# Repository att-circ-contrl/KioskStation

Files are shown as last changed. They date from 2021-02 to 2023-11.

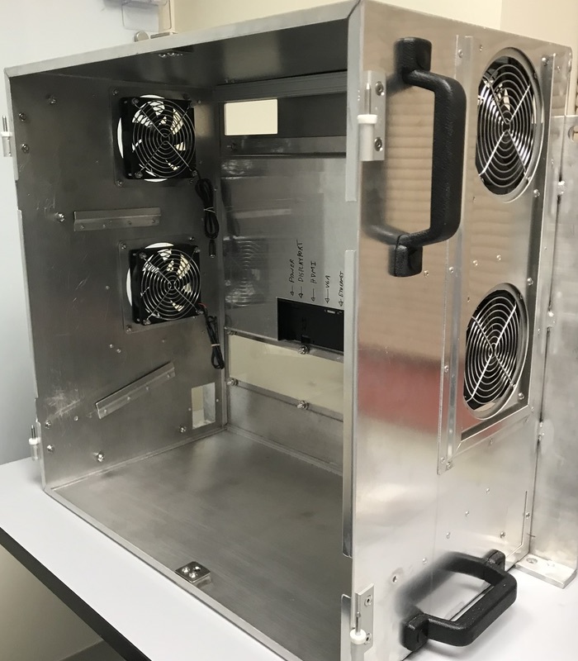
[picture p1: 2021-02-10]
photos/install-20181106/fan-installed.jpg

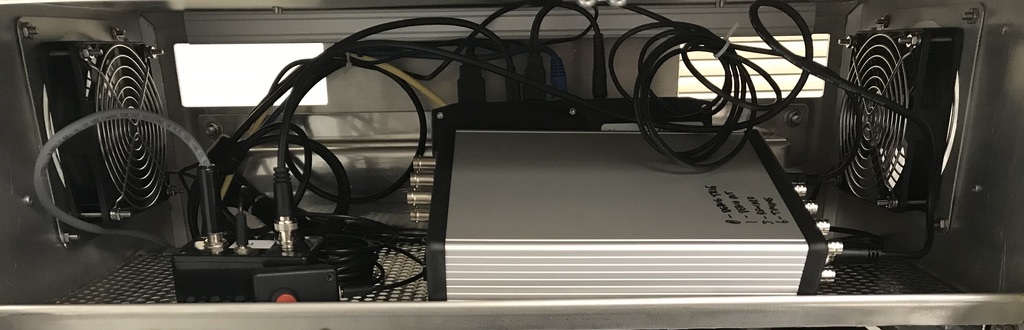
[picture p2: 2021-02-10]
photos/install-20181106/ard-pbox-wiring.jpg

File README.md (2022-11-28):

# "Kiosk Station" NHP Game Kiosk

## Overview

The "Kiosk Station" is an interactive game kiosk intended for use with
non-human primates. The kiosk is mounted to one module of an apartment-cage
(replacing one of the wall panels), allowing a monkey to freely play the
game without direct supervision.

**This repository is a work-in-progress.**
All of the CAD files and auxiliary information needed to make additional
"revision 2" kiosks should be present (in `drawings-ext/rev2-cad-2021`),
but organization could be better.

The "Kiosk Station" project is copyright (c) 2021 by Vanderbilt University,
and is released under the Creative Commons Attribution 4.0 International
License.

## Folders

This repository contains the following directories:

* `datasheets` -- Vendor-supplied datasheets. Under vendor copyright.
* `drawings-ext` --
CAD files and screenshots for various versions of the Kiosk Station.
Component models and documentation provided by third-party component vendors
are under vendor copyright.
* `drawings` -- Assorted mechanical drawings.
* `manual` --
LaTeX source and PDF output for the kiosk user manual (incomplete).
* `notes` -- Assorted notes regarding the kiosk's design and components.
* `photos` -- Representative photos of the kiosk and kiosk equipment.
* `proximity-2017` --
Materials relating to tests of proximity sensors that were to be mounted
on the sipper tube of the kiosk.
* `pump-box` --
Design documents for the control box for the LMI fluid pump used with the
kiosk. The intention is that TTL pulses or user-fob button presses can
trigger delivery of a fluid reward (water or juice) through the sipper tube.
* `reference` --
Assorted reference documents (other than datasheets or vendor-supplied
materials).
* `vendor-docs` --
Vendor-provided documentation (other than datasheets). Under vendor copyright.
* `wiring-diagrams` -- Wiring/cabling diagrams for kiosk-related equipment.

_This is the end of the file._

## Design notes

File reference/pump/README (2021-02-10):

Executive summary:

- Pinout is on page 17 of the manual, control scheme is on page 21.
- Connector type is "M12" circular connector.

- Use their grey cable if possible (p/n 48414).
- White wire is ground, brown is _enable (short to ground), blue is pulse 
(short to ground; pump triggers on release). Black is +15v (use for power),
green is analog control (nc for this pump type).

- Max voltage 24 V, max current 15 mA. They used a 10 kOhm PD in their 
"adapter cable", so actual currents are likely much lower.
- Pulse times must be at least 50 ms.

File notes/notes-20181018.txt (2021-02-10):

From 18 Oct 2018 paper notes:

- Holes in viewport plates should be larger for more alignment slop; some of 
the plates are very difficult to remove due to rubbing on threads.

- Pump mounting brackets should be 1" rather than 1.5" wide, to avoid 
conflict with anything else attached to the 1" extrusion.

- Fan mounts need an adapter plate for 120mm fans (implemented as 6" fans).

- Cannot mount twist-style t-slot cable holders to 1" rail due to enclosure 
sheet metal extending past the edge of the extrusion; trim if possible.

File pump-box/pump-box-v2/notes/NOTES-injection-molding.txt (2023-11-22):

I'm designing the v2 case as something that could be manufactured by
injection molding, in case we want lots of these.

The main difficulty is that it'll have to be 3 pieces rather than 2 pieces,
if we want the cable gland to enter through the end. Entering through a face
could be 2 pieces.

For injection molding, thickness should be uniform (if possible), with a
draft angle of about 4 degrees on vertical surfaces where practical.

For parts to be released from the mold (and for the molds to be machined),
each half of the mold has to be "2.5-d" (no undercuts). This means each half
of the part being made needs to be "2.5-d". "Flying saucer" (with the part
lin on the rim) and "bowl" (with the part line on the lip) shapes are
examples of this type of geometry.

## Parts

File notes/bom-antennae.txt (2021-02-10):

Suitable parts for hooking up a router to an external antenna:

Item			Digikey p/n		Each	Qty	Total

cable 4' RP-SMA RA	JR2R3-L1-4F-ND		34.00	1	34.00
antenna dome RP-SMA	ANT-DB1-WRT-MON-RPS-ND	12.94	1	12.94
Washer 1/2" galv	H840-ND			0.0309	2	0.06

Total:								47.00

Suitable parts for hooking up a Unity computer to an external antenna:

Item			Digikey p/n		Each	Qty	Total

cable 20" IPEX MHF4/SMA	1837-1033-ND		3.25	1	3.25
antenna dome SMA	ANT-DB1-WRT-MON-SMA-ND	12.94	1	12.94
Washer 1/2" galv	H840-ND			0.0309	2	0.06

Total:								16.25

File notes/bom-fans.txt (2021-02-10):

Fan parts from 20181004-digikey:

fan 120mm 12V 34dBA:	259-1472-nd
medical 12V 2A wart:	1145-1240-nd
barrel splitter 2.1mm:	1528-1455-nd
barrel 2.1mm F to wire:	839-1145-nd

From 2021:

fan 80mm 12V 33dBA:	259-1629-nd

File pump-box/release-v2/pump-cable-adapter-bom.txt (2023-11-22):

Bill of materials for the v2 pump control dongle:

Item				Mfg p/n		Digikey p/n		Qty

transistor NPN SOT-23-3		SST3904T116	SST3904T116CT-ND	2

resistor 0805 10 kOhm		RC0805FR-0710KL	311-10.0KCRCT-ND	2

jack audio 3.5mm mono SMT	MJ-3523-SMT-TR	CP-3523MJCT-ND		1

BNC jack (PCB R/A)		0731000154	WM5281-ND		1

terminal block 3.81mm 5pos	284392-5	A98169-ND		1

cable cland PG9			3210		3720-3210-ND		1
(NOTE - 3211 is a fallback option. 3210 is black, 3211 is grey.)

(This is the end of the file.)

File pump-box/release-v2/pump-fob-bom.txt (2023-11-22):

Bill of materials for the v2 pump trigger fob:

Item				Mfg p/n		Digikey p/n		Qty

jack audio 3.5mm mono SMT	MJ-3523-SMT-TR	CP-3523MJCT-ND		1

switch smt 12mm spst		K12SCS1.55NOLFTX	CKN10790CT-ND	1

(This is the end of the file.)

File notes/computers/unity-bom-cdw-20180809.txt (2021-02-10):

Machine (no RAM):  NUC6i7KYK  CDW p/n: 4085713   (543.99 USD)
RAM:  Kingston DDR4 2x4gig  CDW p/n: 4039935   (102.99 USD)
SSD:  (1 TB) Samsung MZ-N6E1T0BW  CDW p/n: 4934196   (239.99 USD)
Network cable:  Tripp Lite 3' Cat5e  CDW p/n: 324473  (2.99 USD)

Unit cost:  889.96 USD

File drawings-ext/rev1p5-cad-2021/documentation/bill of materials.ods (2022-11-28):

name | number | qty per | total
Positioning arm | 47065t361 | 4 | 8
black rubber handle | 13665a27 | 4 | 8
left hinge | 3116a1 | 2 | 4
right hinge | 3116a2 | 2 | 4
slam latch | 171hn01 | 5 | 10
low profile clamp | 84865a22 | 16 | 32
90 bracket | 5537t349 | 2 | 4
surface mount hinge | 1624a52 | 2 | 4
t handle latch | 11055a24 | 1 | 2
t slot extrusion (2 sided) | 47065t551 | 5 | 10
stainless studs ¼-20
stainless studs 10-32 3/8 | CD51032-0375-1 (https://michigan.hybrocosales.com/details/item?itemid=CD51032-0375-1)
Stainless studs 3/8-16 1” | CD53816-1000-1
aluminum studs ¼ -20 3/4” | CD51420-0750-1 (https://michigan.hybrocosales.com/details/item?itemid=CD51420-0750-1)
stainless nuts ¼ -20
stainless nuts 10-32
stainless nuts 3/8 -16
stainless washers ¼
stainless washers 3/8
stainless washers #10
stainless angle 1 ¼ x 1 ¼
stainless angle 1x1
stainless rod ½
stainless rod 3/8
stainless rod ¼
stainless flatbar 1 x 3/16
stainless flatbar 1.5 x 1/8
stainless flatbar 1.5 x 5/16
stainless tubing 1”
stainless sch 40 pipe 3.5”
stainless sq tube ½
stainless rnd tube 1/8”
aluminum flattened expanded
stainless button head bolt ¼ -20 ¾
stainless button head bolt ¼ -20 ½
stainless bolt 3/8-16
Stainless 10-32 button ½
stainless screw #8 5/16
stainless countersink ¼ 20 3/8
stainless countersink10-32 3/8
plexiglas
panels

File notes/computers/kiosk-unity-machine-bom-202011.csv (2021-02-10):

Please save as excel file & upload to Procurement Notification form. |  |  |  | ORDER TOTAL |  | $2,299.88
Enter the ORDER TOTAL amount listed here into the field 'Quote/Line Item Worksheet Total' in the online Procurement Notification form.
Line | Item Catalog Number | Item Description including specs & customizations | Quantity | Unit Price | UoM | Extended Price | Item URL
 |  |  |  |  | Each
 |  |  |  |  | Case/Carton
1 | 5033016 | computer NUC8i7HVK barebones small form factor | 2 | $908.99 | Each | $1,817.98 | https://www.cdw.com/product/intel-next-unit-of-computing-kit-nuc8i7hvk-mini-pc-core-i7-8809g-3.1-gh/5033016
2 | 4934196 | SSD 1 TB 860 EVO | 2 | $149.99 | Each | $299.98 | https://www.cdw.com/product/samsung-860-evo-mz-n6e1t0bw-solid-state-drive-1-tb-sata-6gb-s/4934196
3 | 5109903 | SDRAM DDR4 SODIMM-260 16 GB non-ECC | 2 | $69.99 | Each | $139.98 | https://www.cdw.com/product/kingston-ddr4-16-gb-so-dimm-260-pin-unbuffered/5109903
4 | 324473 | network cable cat5e 3ft | 2 | $2.99 | Each | $5.98 | https://www.cdw.com/product/tripp-lite-3ft-cat5e-cat5-350mhz-blue-snagless-molded-patch-cable-rj45-m-m/324473
5 | 4639758 | cable mini-DP to DP 3ft | 2 | $8.99 | Each | $17.98 | https://www.cdw.com/product/tripp-lite-mini-displayport-to-displayport-adapter-cable-4k-m-m-black-3ft/4639758
6 | 4884365 | cable HDMI 3ft | 2 | $8.99 | Each | $17.98 | https://www.cdw.com/product/tripp-lite-high-speed-hdmi-cable-w-gripping-connectors-4k-m-m-black-3ft/4884365
7 |  |  |  |  |  | $-
8 |  |  |  |  |  | $-
9 |  |  |  |  |  | $-
10 |  |  |  |  |  | $-
11 |  |  |  |  |  | $-
12 |  |  |  |  |  | $-
13 |  |  |  |  |  | $-
14 |  |  |  |  |  | $-
15 |  |  |  |  |  | $-
16 |  |  |  |  |  | $-
17 |  |  |  |  |  | $-
18 |  |  |  |  |  | $-
19 |  |  |  |  |  | $-
20 |  |  |  |  |  | $-
21 |  |  |  |  |  | $-
22 |  |  |  |  |  | $-
23 |  |  |  |  |  | $-
24 |  |  |  |  |  | $-
25 |  |  |  |  |  | $-
26 |  |  |  |  |  | $-
27 |  |  |  |  |  | $-
28 |  |  |  |  |  | $-
29 |  |  |  |  |  | $-
30 |  |  |  |  |  | $-
31 |  |  |  |  |  | $-
32 |  |  |  |  |  | $-
33 |  |  |  |  |  | $-
34 |  |  |  |  |  | $-
35 |  |  |  |  |  | $-
36 |  |  |  |  |  | $-
37 |  |  |  |  |  | $-
38 |  |  |  |  |  | $-
39 |  |  |  |  |  | $-
40 |  |  |  |  |  | $-
41 |  |  |  |  |  | $-
42 |  |  |  |  |  | $-
43 |  |  |  |  |  | $-
44 |  |  |  |  |  | $-
45 |  |  |  |  |  | $-
46 |  |  |  |  |  | $-
47 |  |  |  |  |  | $-
48 |  |  |  |  |  | $-
49 |  |  |  |  |  | $-
50 |  |  |  |  |  | $-
51 |  |  |  |  |  | $-
52 |  |  |  |  |  | $-
53 |  |  |  |  |  | $-
54 |  |  |  |  |  | $-
55 |  |  |  |  |  | $-
56 |  |  |  |  |  | $-
57 |  |  |  |  |  | $-
58 |  |  |  |  |  | $-
59 |  |  |  |  |  | $-
60 |  |  |  |  |  | $-
61 |  |  |  |  |  | $-
62 |  |  |  |  |  | $-
63 |  |  |  |  |  | $-
64 |  |  |  |  |  | $-
65 |  |  |  |  |  | $-
66 |  |  |  |  |  | $-
67 |  |  |  |  |  | $-
68 |  |  |  |  |  | $-
69 |  |  |  |  |  | $-
70 |  |  |  |  |  | $-
71 |  |  |  |  |  | $-
72 |  |  |  |  |  | $-
73 |  |  |  |  |  | $-
74 |  |  |  |  |  | $-
75 |  |  |  |  |  | $-
76 |  |  |  |  |  | $-
77 |  |  |  |  |  | $-
78 |  |  |  |  |  | $-
79 |  |  |  |  |  | $-
80 |  |  |  |  |  | $-
81 |  |  |  |  |  | $-
82 |  |  |  |  |  | $-
83 |  |  |  |  |  | $-
84 |  |  |  |  |  | $-
85 |  |  |  |  |  | $-
86 |  |  |  |  |  | $-
87 |  |  |  |  |  | $-
88 |  |  |  |  |  | $-
89 |  |  |  |  |  | $-
90 |  |  |  |  |  | $-
91 |  |  |  |  |  | $-
92 |  |  |  |  |  | $-
93 |  |  |  |  |  | $-
94 |  |  |  |  |  | $-
95 |  |  |  |  |  | $-
96 |  |  |  |  |  | $-
97 |  |  |  |  |  | $-
98 |  |  |  |  |  | $-
99 |  |  |  |  |  | $-
100 |  |  |  |  |  | $-
 |  |  |  |  |  | $-
 |  |  |  |  |  | $-
 |  |  |  |  |  | $-
 |  |  |  |  |  | $-
 |  |  |  |  |  | $-
 |  |  |  |  |  | $-
 |  |  |  |  |  | $-
 |  |  |  |  |  | $-
 |  |  |  |  |  | $-
 |  |  |  |  |  | $-
 |  |  |  |  |  | $-
 |  |  |  |  |  | $-
 |  |  |  |  |  | $-
 |  |  |  |  |  | $-
 |  |  |  |  |  | $-
 |  |  |  |  |  | $-
 |  |  |  |  |  | $-
 |  |  |  |  |  | $-
 |  |  |  |  |  | $-
 |  |  |  |  |  | $-
 |  |  |  |  |  | $-
 |  |  |  |  |  | $-
 |  |  |  |  |  | $-
 |  |  |  |  |  | $-
 |  |  |  |  |  | $-
 |  |  |  |  |  | $-
 |  |  |  |  |  | $-
 |  |  |  |  |  | $-
 |  |  |  |  |  | $-
 |  |  |  |  |  | $-
 |  |  |  |  |  | $-
 |  |  |  |  |  | $-
 |  |  |  |  |  | $-
 |  |  |  |  |  | $-
 |  |  |  |  |  | $-
 |  |  |  |  |  | $-
 |  |  |  |  |  | $-
 |  |  |  |  |  | $-
 |  |  |  |  |  | $-
 |  |  |  |  |  | $-
 |  |  |  |  |  | $-
 |  |  |  |  |  | $-
 |  |  |  |  |  | $-
 |  |  |  |  |  | $-
 |  |  |  |  |  | $-
 |  |  |  |  |  | $-
 |  |  |  |  |  | $-
 |  |  |  |  |  | $-
 |  |  |  |  |  | $-
 |  |  |  |  |  | $-
 |  |  |  |  |  | $-
 |  |  |  |  |  | $-

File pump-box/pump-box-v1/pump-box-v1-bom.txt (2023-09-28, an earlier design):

Bill of materials for the v1 pump control box:

Item                         Digikey p/n     Unit Price     Qty      Cost

box 3.25x2.25x1.5"           HM113-ND           5.56         1       5.56
box 2x1.5.0.75"              HM375-ND           2.62         1       2.62

transistor NPN TO-92         2N3904FS-ND        0.21         2       0.42

resistor 1/4 W 10 kohm       10.0KXBK-ND        0.10         2       0.20
resistor 1/4 W 3.3 kohm      3.3KXBK-ND         0.10         1       0.10

proto board 1x1"             1568-1652-ND       1.50         1       1.50

screw 4-40 nylon 1/4"        H542-ND            0.09         1       0.09
standoff nylon 4-40 F/F 1/2" 36-1902C-ND        0.70         1       0.70
screw metal 4-40 3/8"        HM1456-ND          0.11         1       0.11

jack BNC panel mount         ARFX1064-ND        2.64         1       2.64
jack audio 1/4" stereo panel SC1563-ND          3.06         1       3.06
plug audio 1/4" stereo       SC1081-ND          4.39         1       4.39
jack audio 3.5mm mono panel  SC238-ND           2.54         2       5.08

cable audio 3.5mm M/M 10'    TL634-ND           4.61         1       4.61

button spst-no panel mount   CW158-ND           4.25         1       4.25

Total:                                                              35.33

NOTE - Digikey M12 cables have the wrong polarization key for the pump. We
need "reverse key" cables.
MEC-5FP-2M from www.mencom.com looks correct.

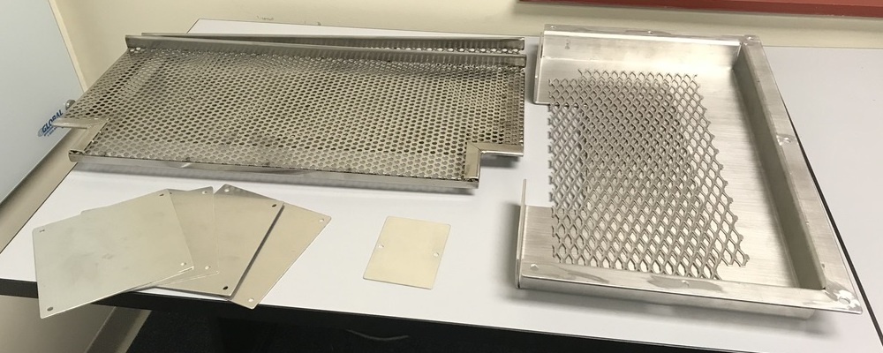
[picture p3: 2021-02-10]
photos/install-20181106/bay-parts.jpg

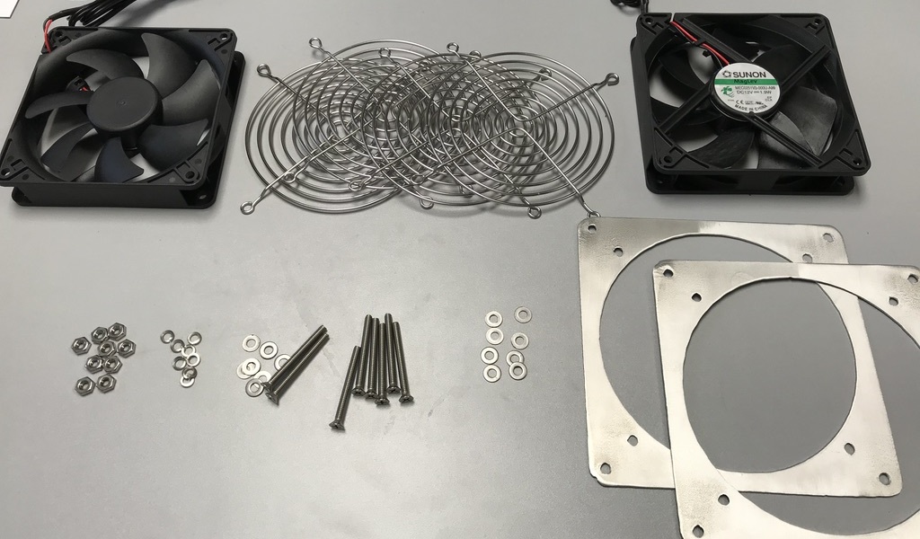
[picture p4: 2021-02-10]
photos/install-20181106/fan-parts.jpg

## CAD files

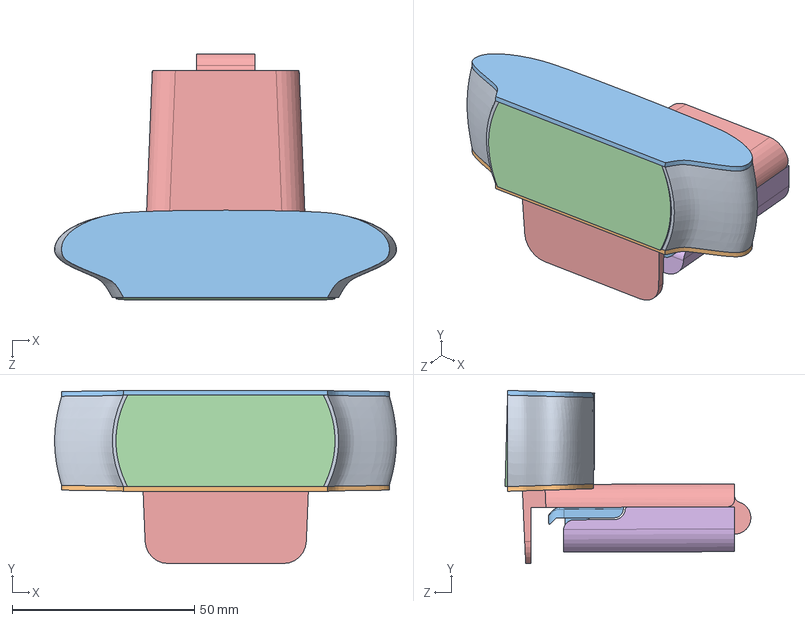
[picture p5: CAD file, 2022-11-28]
drawings-ext/rev1p5-cad-2021/camera/c920.SLDASM
93.8 x 47.5 x 67.5 mm
BOTTOM plate
TOP plate
Pieza4^c920
Top Holder
Pieza6^c920
Speaker^PCB_and_lens x 2
Lens Mount^PCB_and_lens
Pieza4^PCB_and_lens
Pieza8^c920

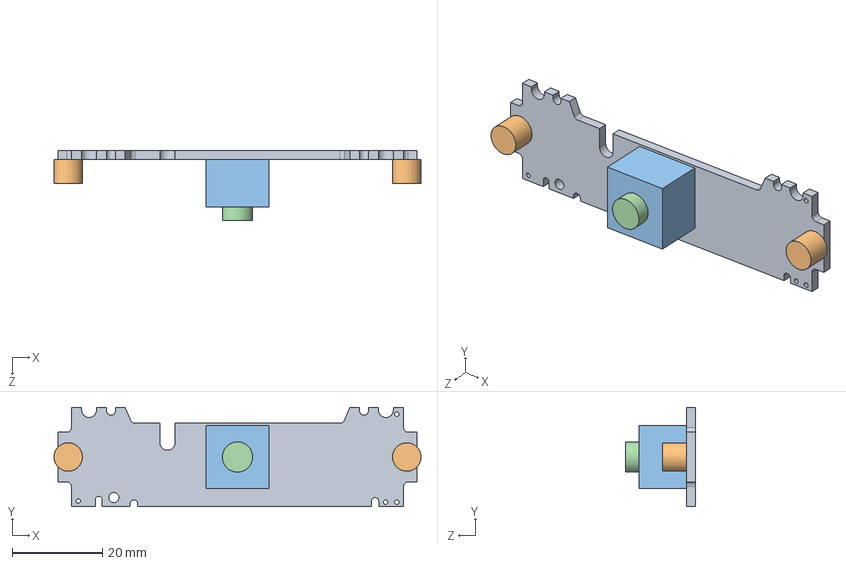
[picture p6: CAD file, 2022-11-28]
drawings-ext/rev1p5-cad-2021/camera/PCB_and_lens.SLDASM
81.3 x 22.0 x 15.5 mm
PCB^PCB_and_lens
Speaker^PCB_and_lens x 2
Lens Mount^PCB_and_lens
Pieza4^PCB_and_lens

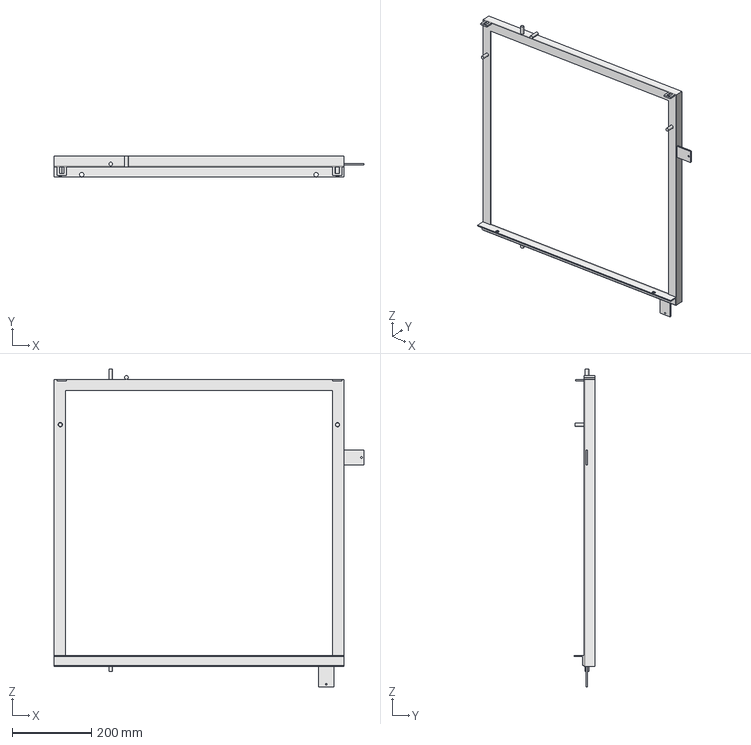
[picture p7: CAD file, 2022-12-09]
cad/adapter-rev2/adapter-rev2.fcstd
781.1 x 54.0 x 800.1 mm

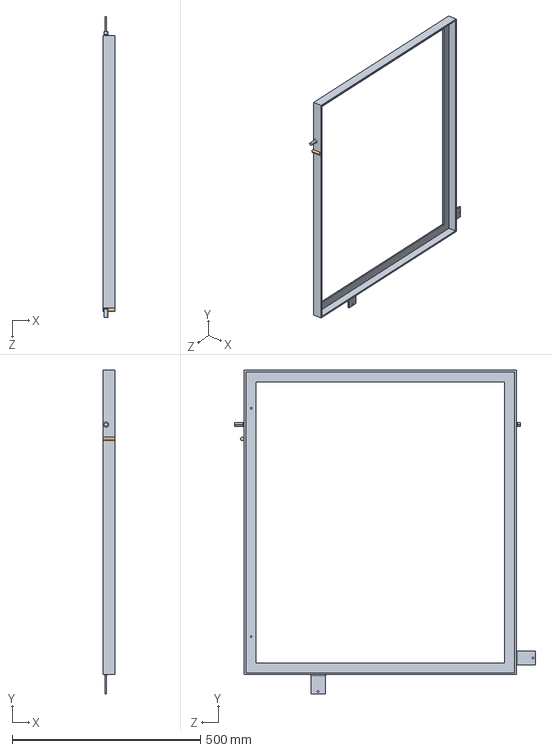
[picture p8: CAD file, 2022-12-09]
drawings-ext/seattle-20221208/DECkiosk-2018051033.step
31.8 x 860.4 x 800.1 mm

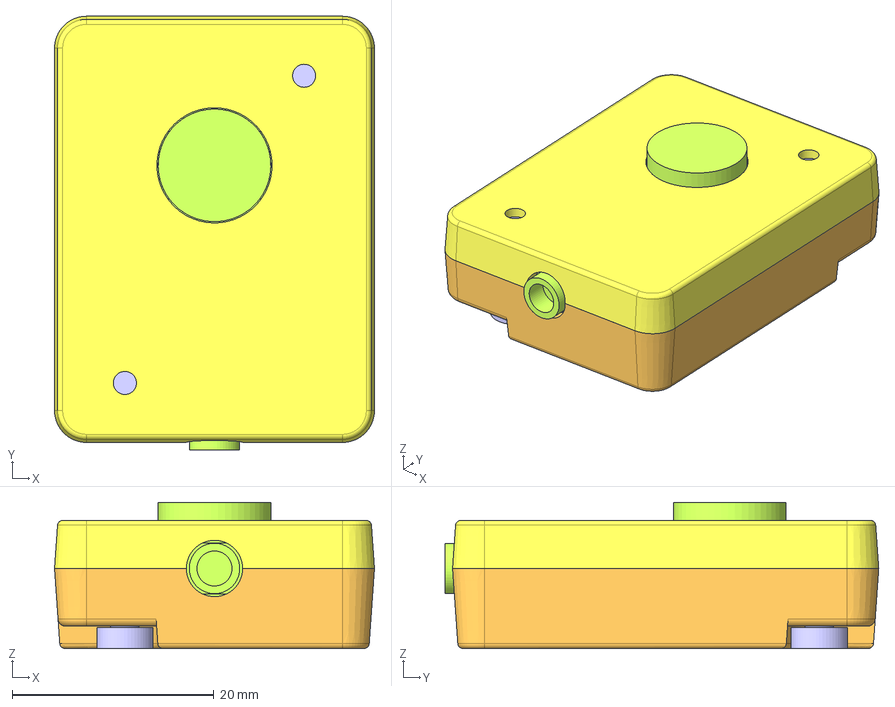
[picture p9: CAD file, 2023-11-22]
pump-box/pump-box-v2/cad/pump-fob-case-v2.fcstd
31.7 x 43.0 x 14.5 mm
populated pcb clone
bottom shell clone
top shell clone
mockup screw 1
mockup screw 2

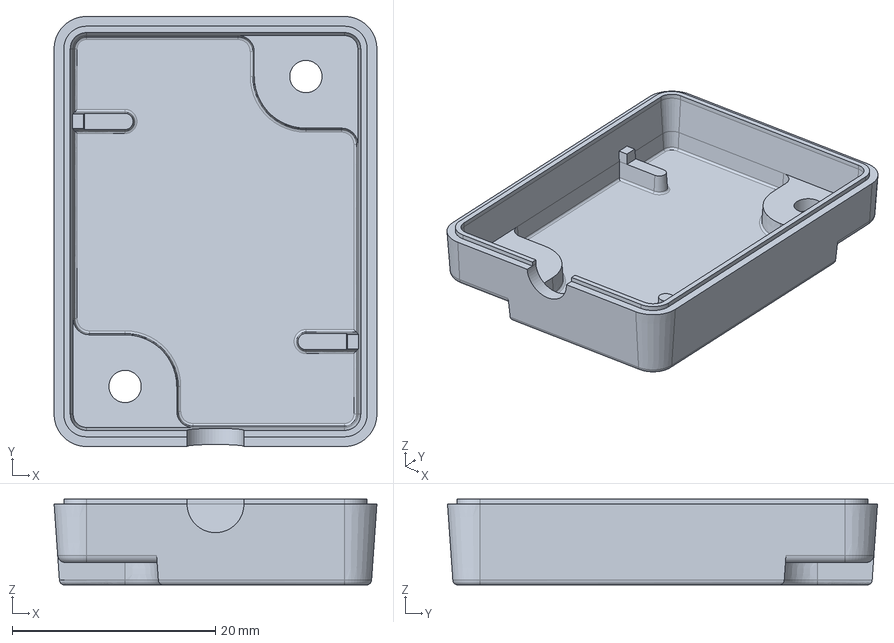
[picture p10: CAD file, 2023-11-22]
pump-box/pump-box-v2/iges/pump-fob-v2-shell-bottom.iges
31.8 x 42.3 x 8.45 mm

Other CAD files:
cad/adapter-rev2/exported/adapter-rev2-frame.step
drawings-ext/rev1p5-cad-2021/arm/PARTserver02018062215211850310062192d056f/CMM-14082.dwg
drawings-ext/rev1p5-cad-2021/bottle/bottle.dwg
drawings-ext/rev1p5-cad-2021/breakdown/frame.dwg
drawings-ext/rev1p5-cad-2021/cutting patterns/13_2 alum 0625.dxf
drawings-ext/rev1p5-cad-2021/key lock/lock.dwg
drawings-ext/rev1p5-cad-2021/mounting bracket/low profile clamp.dwg
drawings-ext/rev1p5-cad-2021/pellet dispenser/pellet filler place holder.dwg
drawings-ext/rev1p5-cad-2021/straw.dwg
pump-box/pump-box-v2/meshes/pump-fob-v2-shell-bottom.stl
cad/adapter-rev2/exported/adapter-rev2-frame.iges
drawings-ext/rev1p5-cad-2021/Kiosk Test Station.stl
drawings-ext/rev1p5-cad-2021/cutting patterns/10_2 stainless 7 ga.dxf
drawings-ext/rev1p5-cad-2021/cutting patterns/11_1 stainless 11 ga.dxf
drawings-ext/rev1p5-cad-2021/cutting patterns/12_2 alum 1875.dxf
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

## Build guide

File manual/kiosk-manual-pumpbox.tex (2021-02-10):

% Kiosk manual - Pump control box.
% Written by Christopher Thomas.

\chapter{Pump Control Box}
\label{sect-pumpbox}

\section{Overview}
\label{sect-pumpbox-over}

The pump control box allows the reward pump to be controlled by a 5V
active-high signal over BNC for automated rewards and by pressing a button 
on a fob for manual rewards. A schematic for the pump control box is
shown in Figure \ref{fig-pumpbox-schem}.

\textbf{NOTE} -- While a similar 1/4'' plug is used for old and new boxes,
cable plugs wired for old control boxes are \textbf{NOT} compatible with
the current control box, and vice versa. New cables use a stereo plug with
+15~V on the ring.

A diagram of box cutouts is shown in Figure \ref{fig-pumpbox-boxes}. A bill
of materials is given in Table \ref{tab-pumpbox-bom}.

\begin{figure}[h]
\begin{center}
\includegraphics[width=0.95\columnwidth]
{figs-pump/pump-box-v1-schem.pdf}
\end{center}
\caption{Pump control box schematic.}
\label{fig-pumpbox-schem}
\end{figure}

\begin{figure}[h]
\begin{center}
\includegraphics[width=0.8\columnwidth]
{figs-pump/pump-box-v1-mech-notitle.pdf}
\end{center}
\caption{Pump control box cutouts.}
\label{fig-pumpbox-boxes}
\end{figure}

\begin{table}[h]
\begin{center}
\begin{tabular}{llr}
\hline
\textbf{Item} & \textbf{Digikey p/n} & \textbf{Quantity} \\
\hline
box 3.25x2.25x1.5''		& HM113-ND	& 1	\\
box 2x1.5.0.75''		& HM375-ND	& 1	\\
transistor NPN TO-92		& 2N3904FS-ND	& 2	\\
resistor 1/4 W 10 kohm		& 10.0KXBK-ND	& 2	\\
resistor 1/4 W 3.3 kohm		& 3.3KXBK-ND	& 1	\\
proto board 1x1''		& 1568-1652-ND	& 1	\\
screw 4-40 nylon 1/4''		& H542-ND	& 1	\\
standoff nylon 4-40 F/F 1/2''	& 36-1902C-ND	& 1	\\
screw metal 4-40 3/8''		& HM1456-ND	& 1	\\
jack BNC panel mount		& ARFX1064-ND	& 1	\\
jack audio 1/4'' stereo panel	& SC1563-ND	& 1	\\
plug audio 1/4'' stereo		& SC1081-ND	& 1	\\
jack audio 3.5mm mono panel	& SC1455-ND	& 2	\\
cable audio 3.5mm M/M 10'	& TL634-ND	& 1	\\
button spst-no panel mount	& CW158-ND	& 1	\\
cable M12 rev key to wire	& $^\dagger$	& 1	\\
\hline
\multicolumn{3}{p{0.8\columnwidth}}
{$^\dagger$Sold by LMI as part number 48414; may be sourced more cheaply as
MEC-5FP-2M from www.mencom.com. These have a ``5 pole reverse-keyed'' M12
connector.} \\
\end{tabular}
\end{center}
\caption{Pump control box bill of materials.}
\label{tab-pumpbox-bom}
\end{table}

\clearpage
\section{Pump Cable Plug}
\label{sect-pumpbox-plug}

Assembly steps for the pump cable plug are shown below. Use of
$\frac{1}{8}$'' heat shrink tubing is strongly recommended to avoid shorts
within the plug housing.

\begin{itemize}
%
\item Trim wires to appropriate lengths, and feed cable through backshell.

\includegraphics[width=0.8\columnwidth]
{photos/pump-box-20181030/plug-started.jpg}

\item Cap green wire with heat shrink, twist brown and white wires together
and tin, tin blue wire, solder resistor to black wire.

\includegraphics[width=0.8\columnwidth]
{photos/pump-box-20181030/plug-midway.jpg}

\item Cover resistor connection with heat shrink, solder blue wire,
resistor lead, and brown/white wire pair to appropriate lugs.

\includegraphics[width=0.8\columnwidth]
{photos/pump-box-20181030/plug-done.jpg}

\item Crimp collar around wires and screw backshell on to plug.

\textbf{NOTE} - ideally the wires would be short enough that the collar is
crimped to the jacket rather than to the wire bundle.
%
\end{itemize}

\clearpage
\section{Circuit Board}
\label{sect-pumpbox-board}

Assembly steps for the circuit board are shown below. The prototyping board
trace pattern and one possible layout are shown in Figure
\ref{fig-pumpbox-protoboard}.

\begin{figure}
\begin{center}
\begin{tabular}{ccc}
\includegraphics[height=2in]
{figs-pump/pump-box-v1-breadboard.pdf}
& ~ &
\includegraphics[height=2in]
{figs-pump/pump-box-v1-bblayout.pdf}
\\
\end{tabular}
\end{center}
\caption{Prototyping board and one possible pump control circuit layout.}
\label{fig-pumpbox-protoboard}
\end{figure}

\begin{itemize}
%
\item Solder transistors and resistors.

\includegraphics[height=2in]
{photos/pump-box-20181112/board-comps.jpg}

\item Solder signal and power wires. Marking is encouraged to keep track
of which are which.

\includegraphics[height=2in]
{photos/pump-box-20181112/board-orange.jpg}

\clearpage
\item Solder ground wires.

\includegraphics[height=2in]
{photos/pump-box-20181112/board-black.jpg}

\item Solder jacks to wires. Make sure to thread BNC hardware over the BNC
signal wire and to insert the BNC connector in the faceplate before soldering.

\includegraphics[height=3in]
{photos/pump-box-20181112/board-conns.jpg}

\item Screw circuit board to faceplate.

\includegraphics[height=2in]
{photos/pump-box-20181030/board-done.jpg}
%
\end{itemize}

%
% This is the end of the file.

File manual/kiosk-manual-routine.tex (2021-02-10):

% Kiosk manual - Routine activities.
% Written by Christopher Thomas.

\chapter{Routine Activities}
\label{sect-routine}

\section{Startup and Shutdown}
\label{sect-routine-startupdown}

To power on the electronics bay equipment:

\begin{itemize}
%
\item Turn on the leftmost power bar, and check that the rightmost one
(plugged into the left bar) is also turned on.
%
\item Check that the fans have spun up. They should turn on within a few 
seconds of receiving power.
%
\item Check that the wireless gateway is on (there should be visible lights 
blinking).

If there are no lights, check that the gateway's power button is 
turned on (if it has one). This is the \textbf{large, exposed} button - do 
not press any small or inset buttons (those either reset the gateway to 
default settings or tell it to use an insecure reconfiguration method - 
both are bad).
%
\item Press and hold the NeuroCam machine's power button until it lights up
and the machine's fan spins up.

This should only take about a second. Do not hold it for longer than 3
seconds - holding it 4 seconds or longer forces an immediate shutdown, which
can cause corruption.
%
\item Press and hold the Unity machine's power button until it lights up and
the machine's fan spins up.

Per previous entry, this should only take about a second.
%
\item Check that the small monitor and the touch screen are both showing
a Windows boot or login screen.

If either one is not showing a screen, check that it's powered on.
%
\item Check that you can access the NeuroCam gateway, and that you can
access the NeuroCam's control web page.

The NeuroCam takes 30-60 seconds to boot, so be sure to leave sufficient
time before accessing it.
%
\item Once everything's running properly, close and lock the electronics 
bay doors.
%
\end{itemize}

\clearpage
To safely shut down the electronics bay equipment:

\begin{itemize}
%
\item Log in to the NeuroCam's web page over the wireless network. Click
the ``shutdown'' button.
%
\item Check that the NeuroCam's power light turns off. This may take
several seconds.

\begin{itemize}
\item If the NeuroCam does not power off, it can be forced to power down by
pressing and holding the power button for 4-5 seconds.

\textbf{NOTE} - This may cause data corruption and other problems, so try to
avoid this if possible.
\end{itemize}
%
\item If the Unity machine is logged in:
\begin{itemize}
\item \fixme{key sequence for power-off goes here}.
\end{itemize}
%
\item If the Unity machine is not logged in:
\begin{itemize}
\item Press a harmless key (such as ``shift'') to wake up the display.
\item Press ``tab'' until the power icon is highlighted (this will take 
multiple keystrokes).
\item Hit ``enter'' to expand the power menu.
\item Use the up and down cursor keys to highlight ``Shut Down''.
\item Hit ``enter''.
\end{itemize}
%
\item Check that the Unity machine's power light turns off. This may take
several seconds.

\begin{itemize}
\item If the Unity machine does not power off, it can be forced to shut down
per above. This may cause data corruption and other problems, as noted.
\end{itemize}
%
\item Locate the power switch on the left power bar (the one whose cord
goes outside), and turn it off.
%
\item Once everything's shut down, close and lock the electronics bay doors.
%
\end{itemize}

%
% This is the end of the file.

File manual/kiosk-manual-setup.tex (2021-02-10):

% Kiosk manual - Installation and setup.
% Written by Christopher Thomas.

\chapter{Kiosk Setup}
\label{sect-setup}

\section{Checklist}
\label{sect-setup-checklist}

First-time kiosk setup involves assembling fittings on the kiosk housing 
and installing and cabling electronic equipment inside the electronics bay.
A summary of the steps involved is shown below; photographs and additional
notes are given in Section \ref{sect-setup-howto}.
A cabling diagram for the kiosk is shown in Figure \ref{fig-kiosk-cabling}.

Initial mechanical work:
\begin{itemize}
\item Separate the kiosk face from the electronics bay.
\item With the kiosk face:
\begin{itemize}
\item Remove the outer viewport window from ports that will have cameras
installed.
\item Remove both viewport windows from the port that will have the
cleaning hatch installed.
\item Remove the pump bracket from the side which has the cleaning port.
\item Install the cleaning hatch in its port.
\item Install the pump mounting plate on the remaining pump bracket. The pump
is away from the face of the kiosk, towards the direction of the electronics
bay.
\item Install light filter plates on the viewport windows that will have
cameras. The synchronization LEDs should be close to the camera mounting
arms.
\end{itemize}
\item With the electronics bay:
\begin{itemize}
\item Remove internal shelves.
\item Remove ventilation grilles.
\item Remove fan dummy panels from either the top level or both levels
(for mounting two or four fans, respectively).
\item Remove the external wiring panel from the side nearest the pump.
\item Remove the monitor tray.
\item Seat the touch screen in the monitor tray. Annotate the back of the
monitor tray to show connector locations.
\item Install the monitor and tray in the electronics bay.
\item Install the fans and fan guards.
\item Line the ventilation grilles with HVAC tape to render them glove-safe.
\item Cut filter pads and install the ventilation grilles with filters in
the electronics bay.
\end{itemize}
\end{itemize}

Electronics work:
\begin{itemize}
\item \textbf{NOTE} - This does not include eye-tracker installation.
Power cabling is placed in the eye-tracker bay.
\item \textbf{NOTE} - During each cabling step, excess cable length should
be coiled and zip-tied, and routed cables should be zip-tied to cable mounts
where appropriate.
\item Install power distribution bars at the bottom of the bay (turned off).
\item Reinstall bay shelves.
\item Install fan power plug and connect fans.
\item Install touch screen power supply. Connect power, display, and USB
cables to the touch screen.
\item Install small monitor, keyboard, and mouse on the right-hand side of
the middle shelf. Install monitor power supply in the bottom of the bay.
Route data cables to the top shelf.
\item Install router with two ethernet cables connected to LAN ports on the
left-hand side of the middle shelf. Install router power supply in the 
bottom of the bay. Route ethernet cables to the top shelf. Ensure that the
router's power switch is turned on, if it has one.
\item Install Neurarduino on the top shelf, left-hand side.
\item Install pump reward box on the top shelf, left-hand side. Cable the
pump reward box to the Neurarduino.
\item Install pump reward fob. Use hook-and-loop cable ties to hang it from
the electronics bay carrying handle on the pump side of the unit. Cable the
fob to the pump reward box.
\item Install the Unity machine's power supply in the bottom of the bay.
Route it to the left-hand side of the top shelf.
\item Install Unity machine on top of the Neurarduino. Attach Unity machine
cable connections (which should already be routed to the top shelf).
\item Install LED box on the top shelf, right-hand side. Route BNC cables 
from the LED box out appropriate camera cabling ports; do not coil the 
LED BNC cables yet.
\item Install the NeuroCam machine's power supply in the bottom of the bay.
Route it to the right-hand side of the top shelf.
\item Install NeuroCam and NeuroCam USB hub. Cable the LED box to the
USB hub and the USB hub to the NeuroCam. Attach the NeuroCam power and
ethernet cables.
\end{itemize}

Electronics tests:
\begin{itemize}
\item Turn on power bar. Press power switches on Unity and NeuroCam
computers. Wait 60 seconds for machines to boot.
\item Check that the Unity machine's login display is shown on the touch 
screen and on the small monitor.
\item Check that an authorized machine can connect to the NeuroCam via the
kiosk's router.
\item Perform graceful shutdowns of the Unity machine and NeuroCam machine.
\item Turn off power bar.
\end{itemize}

Final mechanical work:
\begin{itemize}
\item Reattach the kiosk face to the electronics bay.
\item Install cameras.
\item Screw pump control cable on to pump. Use pliers for this.
\item Install pump.
\item Connect LED BNC cables to camera port LEDs. Coil and zip-tie excess 
cabling \textit{inside} the electronics bay. Do \textbf{not} zip-tie BNC
cables to the kiosk face exterior frame unless this is unavoidable. If it
is unavoidable, keep the zip-ties loose enough that they can be cut without
damaging the BNC cables.
\item Connect camera USB cables to the NeuroCam computer. Coil excess
cabling \textit{inside} the electronics bay. Zip-tie the coils, but do
\textbf{not} zip-tie the coils or cables to cable mounts (it must be possible
to disconnect and withdraw the camera USB cables). Exterior camera cables
may be zip-tied to the kiosk face's frame.
\item Connect the pump control cable to the pump box. Coil excess cabling
\textit{inside} the electronics bay. Zip-tie the coils, but do \textbf{not}
zip-tie the coils or cables to cable mounts (it must be possible to
disconnect and withdraw the pump control cable).
\item Zip-tie cables that pass through the lower exterior cable entry port
to the adjacent handle. Keep this loose enough that it can be cut without
damaging the cables.
\item Replace camera cover.
\item Install pump hoses.
\item Mount the kiosk so that the underside is accessible.
\item Install sipper tube.
\item Make remaining pump hose connections.
\end{itemize}

\begin{figure}[h]

\caption{Kiosk cabling daigram.}
\label{fig-kiosk-cabling}
\end{figure}

\clearpage
\section{Kiosk Assembly Notes}
\label{sect-setup-howto}

%
%
\subsection{Viewports and Hatch}
\label{sect-setup-howto-viewports}

\begin{tabular}{ccc}
\includegraphics[width=0.4\columnwidth]
{photos/install-20181106/face-before.jpg} &
~~~ &
\includegraphics[width=0.4\columnwidth]
{photos/install-20181106/hatch.jpg} \\
\end{tabular}

%
%
\clearpage
\subsection{Light Filters and Cameras}
\label{sect-setup-howto-lightfilt}

The LEDs should be as close as possible to the camera mounts. The cameras
must have LEDs in their field of view when in their final positions.

\begin{tabular}{ccc}
\includegraphics[height=0.55\columnwidth]
{photos/install-20181106/lightfilts.jpg} &
~~~ &
\includegraphics[height=0.55\columnwidth]
{photos/install-20181106/cameras.jpg} \\
\end{tabular}

%
%
\clearpage
\subsection{Electronics Bay Prep}
\label{sect-setup-howto-bay}

\begin{tabular}{ccc}
\includegraphics[width=0.4\columnwidth]
{photos/install-20181106/bay-before.jpg} &
~~~ &
\includegraphics[width=0.4\columnwidth]
{photos/install-20181106/bay-stripped.jpg} \\
 & ~ & \\
\multicolumn{3}{c}{%
\includegraphics[width=0.85\columnwidth]
{photos/install-20181106/bay-parts.jpg}%
} \\
\end{tabular}

%
%
\clearpage
\subsection{Touch-Screen Tray}
\label{sect-setup-howto-touch}

\begin{tabular}{ccc}
\includegraphics[height=0.45\columnwidth]
{photos/install-20181106/ts-installed.jpg} &
~~~ &
\includegraphics[height=0.45\columnwidth]
{photos/install-20181106/ts-labels.jpg} \\
\end{tabular}

%
%
\clearpage
\subsection{Fans}
\label{sect-setup-howto-fans}

The photographed version of the kiosk needed adapter plates to mount the
fans. Later versions mount the fans directly to the electronics cabinet.

\textbf{NOTE} - Fans on one side blow into the electronics bay (intake fans),
and fans on the other side blow out of the electronics bay (exhaust fans).
One pair of fans has the stickers facing in and one pair has the stickers
facing out.

\begin{center}
\begin{tabular}{ccc}
\includegraphics[height=0.3\columnwidth]
{photos/install-20181106/fan-parts.jpg} &
~~~ &
\includegraphics[height=0.3\columnwidth]
{photos/install-20181106/fan-screws.jpg} \\
\end{tabular}

\begin{tabular}{ccc}
\includegraphics[height=0.6\columnwidth]
{photos/install-20181106/fan-assembled.jpg} &
~~~ &
\includegraphics[height=0.6\columnwidth]
{photos/install-20181106/fan-installed.jpg} \\
\end{tabular}
\end{center}

%
%
\clearpage
\subsection{Air Filters}
\label{sect-setup-howto-airfilt}

\begin{tabular}{ccc}
\multicolumn{3}{c}{%
\includegraphics[height=0.5\columnwidth]
{photos/install-20181106/air-taped.jpg}%
} \\
 & ~ & \\
\includegraphics[height=0.5\columnwidth]
{photos/install-20181106/air-batting.jpg} &
~~~ &
\includegraphics[height=0.5\columnwidth]
{photos/install-20181106/air-installed.jpg} \\
\end{tabular}

%
%
\clearpage
\subsection{Power Bars and Shelves}
\label{sect-setup-howto-power}

\textbf{NOTE} - The eye-tracker is not installed in the photographed version
of the kiosk. Power cabling is placed in the eye-tracker bay.

\begin{center}
\includegraphics[width=0.9\columnwidth]
{photos/install-20181106/power.jpg}
\end{center}

%
%
\clearpage
\subsection{Small Monitor, Keyboard, and Mouse}
\label{sect-setup-howto-smallmon}

\textbf{NOTE} - The setup photographed did not have a mouse at the time of
installation. A keyboard with integrated touchpad or other pointing device
may be preferable.

\begin{center}
\includegraphics[width=0.9\columnwidth]
{photos/install-20181106/small-mon.jpg}
\end{center}

%
%
\clearpage
\subsection{Wireless Gateway}
\label{sect-setup-howto-router}

\textbf{NOTE} - The antennae for the wireless gateway should be far away
from the metal walls, and nearby cabling should never run parallel to the
antennae.

\begin{center}
\includegraphics[width=0.9\columnwidth]
{photos/install-20181106/small-mon-gateway.jpg}
\end{center}

%
%
\clearpage
\subsection{Neurarduino and Pump Control Box}
\label{sect-setup-howto-ard}

\begin{center}
\includegraphics[width=0.9\columnwidth]
{photos/install-20181106/ard-pbox-wiring.jpg}
\end{center}

%
%
\subsection{Unity Machine}
\label{sect-setup-howto-unity}

\begin{center}
\begin{tabular}{c}
\includegraphics[width=0.6\columnwidth]
{photos/install-20181106/unity-wiring.jpg} \\
\includegraphics[width=0.8\columnwidth]
{photos/install-20181106/ard-unity-placement.jpg} \\
\end{tabular}
\end{center}

%
%
\clearpage
\subsection{LED Box}
\label{sect-setup-howto-ledbox}

\begin{center}
\includegraphics[width=0.9\columnwidth]
{photos/install-20181106/led-box.jpg}
\end{center}

%
%
\subsection{NeuroCam Machine}
\label{sect-setup-howto-neurocam}

\begin{center}
\includegraphics[width=0.9\columnwidth]
{photos/install-20181106/led-ncam-placement.jpg}
\end{center}

%
%
\clearpage
\subsection{External Cabling and Pump}
\label{sect-setup-howto-extcable}
\label{sect-setup-howto-pump}

\begin{tabular}{ccc}
\includegraphics[height=0.5\columnwidth]
{photos/install-20181106/ext-cabling.jpg} &
~~~ &
\includegraphics[height=0.5\columnwidth]
{photos/install-20181106/pump.jpg} \\
\end{tabular}

%
%
\subsection{Camera Cover}
\label{sect-setup-howto-cover}

\begin{tabular}{ccc}
\includegraphics[height=0.47\columnwidth]
{photos/install-20181106/cover-front.jpg} &
~~~ &
\includegraphics[height=0.47\columnwidth]
{photos/install-20181106/cover-back.jpg} \\
\end{tabular}

%
%
\clearpage
\subsection{Pump Hoses}
\label{sect-setup-howto-hoses}

\fixme{Need photos for this.}

%
% This is the end of the file.

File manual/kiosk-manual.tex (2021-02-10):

% Kiosk manual - Top level
% Written by Christopher Thomas.

\documentclass[letterpaper,11pt]{report}
\usepackage[letterpaper]{geometry}
\usepackage{graphicx}
\usepackage{verbatim}
\usepackage{float} % Needed for capital H option.

\geometry{nohead,footskip=0.3in,margin=0.75in}

% Force my paragraph style, darnit.
\usepackage{indentfirst}
\setlength{\parskip}{\baselineskip}

% Custom macros.
\newcommand{\fixme}[1]{\textbf{FIXME: #1}}

% Document body.
\begin{document}

% Title page.

\pagestyle{empty}

\begin{center}
%
\vspace*{1in}
{\Huge \bfseries Kiosk User Guide} \\
{\footnotesize Written by Christopher Thomas -- \today.} \\
%
\vspace*{1in}
\includegraphics[width=0.7\columnwidth]
{photos/install-20181106/cover-front.jpg}
%
\end{center}
%
\clearpage
%
\pagestyle{plain}
\pagenumbering{roman}
\setcounter{page}{1}
%
\tableofcontents
%
\clearpage
\pagestyle{plain}
\setcounter{page}{1}
\pagenumbering{arabic}
% NOTE - "\thispagestyle" is used for part and chapter beginning pages,
% and overrides \pagestyle. Redefine it to be harmless.
\renewcommand{\thispagestyle}[1]{}

% Not using "parts" for now; just chapters.

% Daily use, and accessories (if we make any).
\input{kiosk-manual-routine}
\input{kiosk-manual-setup}
\input{kiosk-manual-pumpbox}

\end{document}

%
% This is the end of the file.

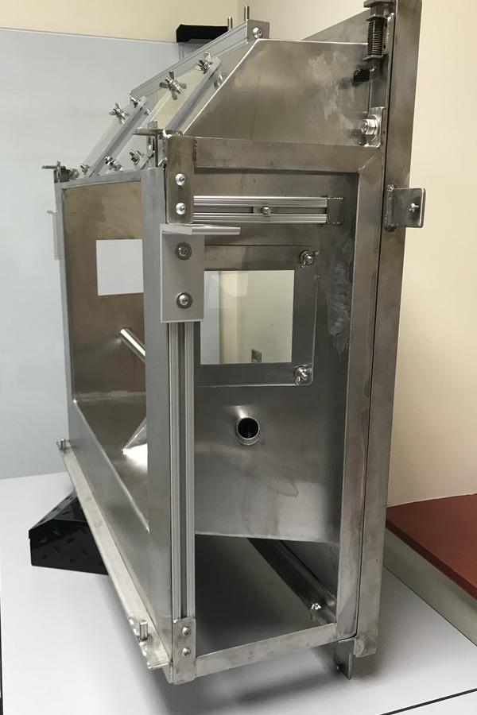
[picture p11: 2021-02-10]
photos/install-20181106/face-before.jpg

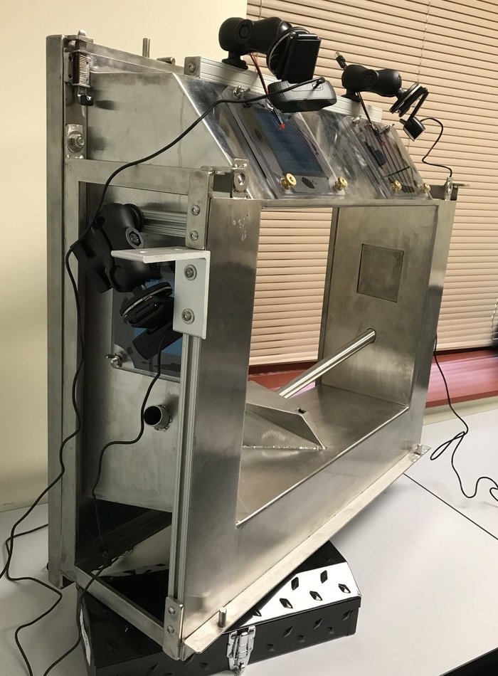
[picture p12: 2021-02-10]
photos/install-20181106/cameras.jpg

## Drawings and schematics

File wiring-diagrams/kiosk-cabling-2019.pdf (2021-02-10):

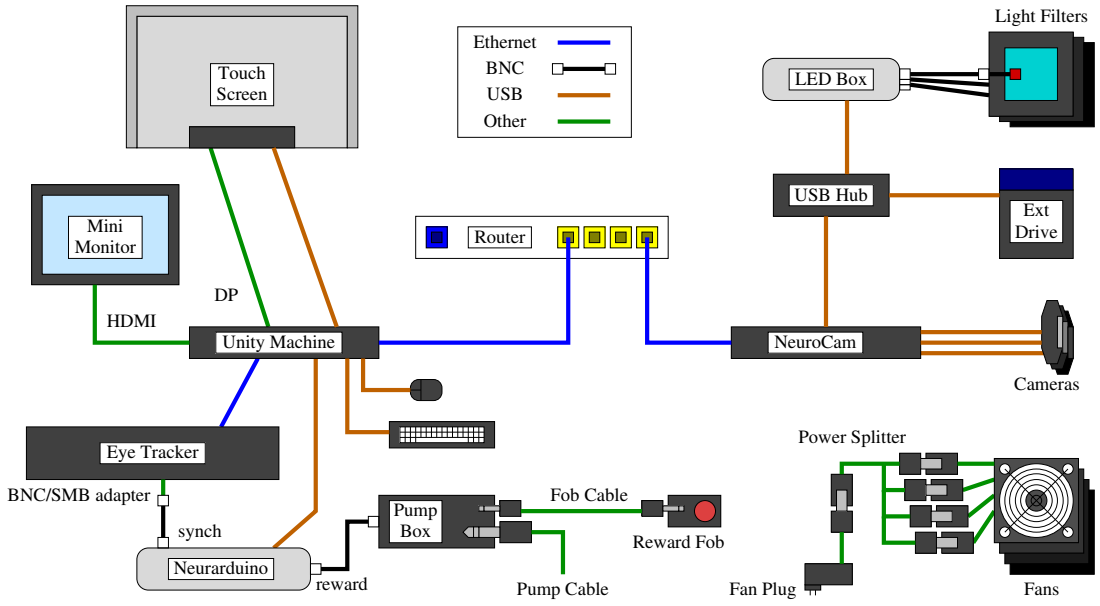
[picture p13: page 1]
Light Filters; LED Box; USB Hub; Ext Drive; Cameras; Unity Machine; NeuroCam; Touch Screen; Mini Monitor; Eye Tracker; Neurarduino; Box; Pump; Fans; Reward Fob; Router; Other; USB; BNC; Ethernet; Pump Cable; HDMI; reward; synch; Fob Cable; Power Splitter; Fan Plug

BNC/SMB adapter

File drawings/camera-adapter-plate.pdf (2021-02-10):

## Camera Adapter Plate

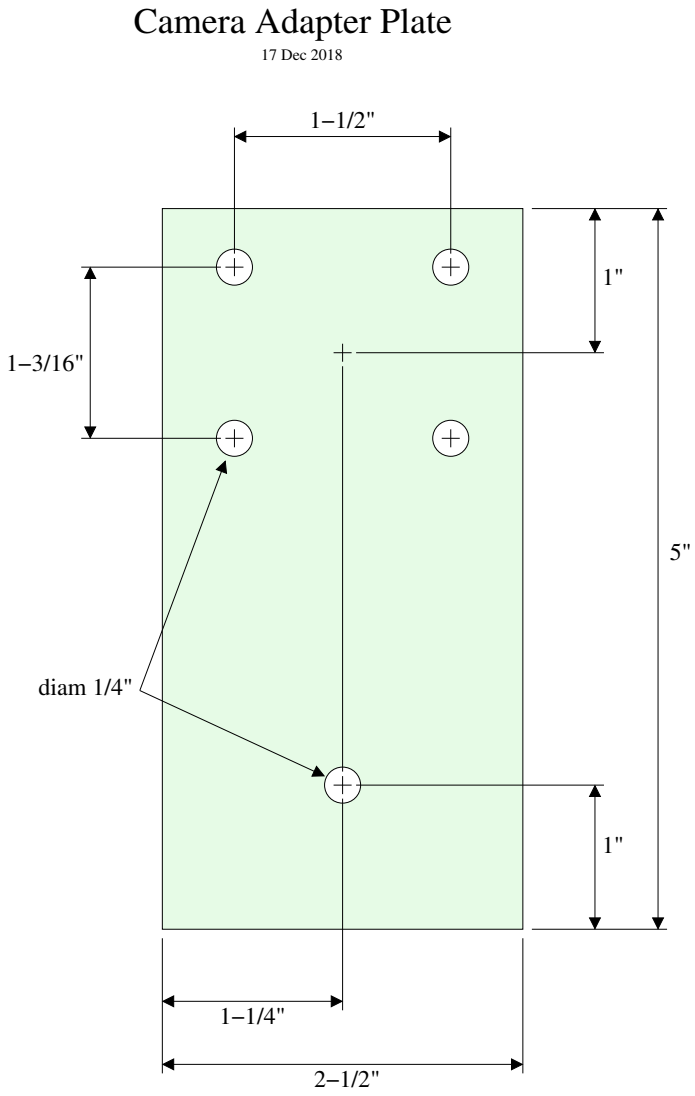
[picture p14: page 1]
diam 1/4"; 17 Dec 2018

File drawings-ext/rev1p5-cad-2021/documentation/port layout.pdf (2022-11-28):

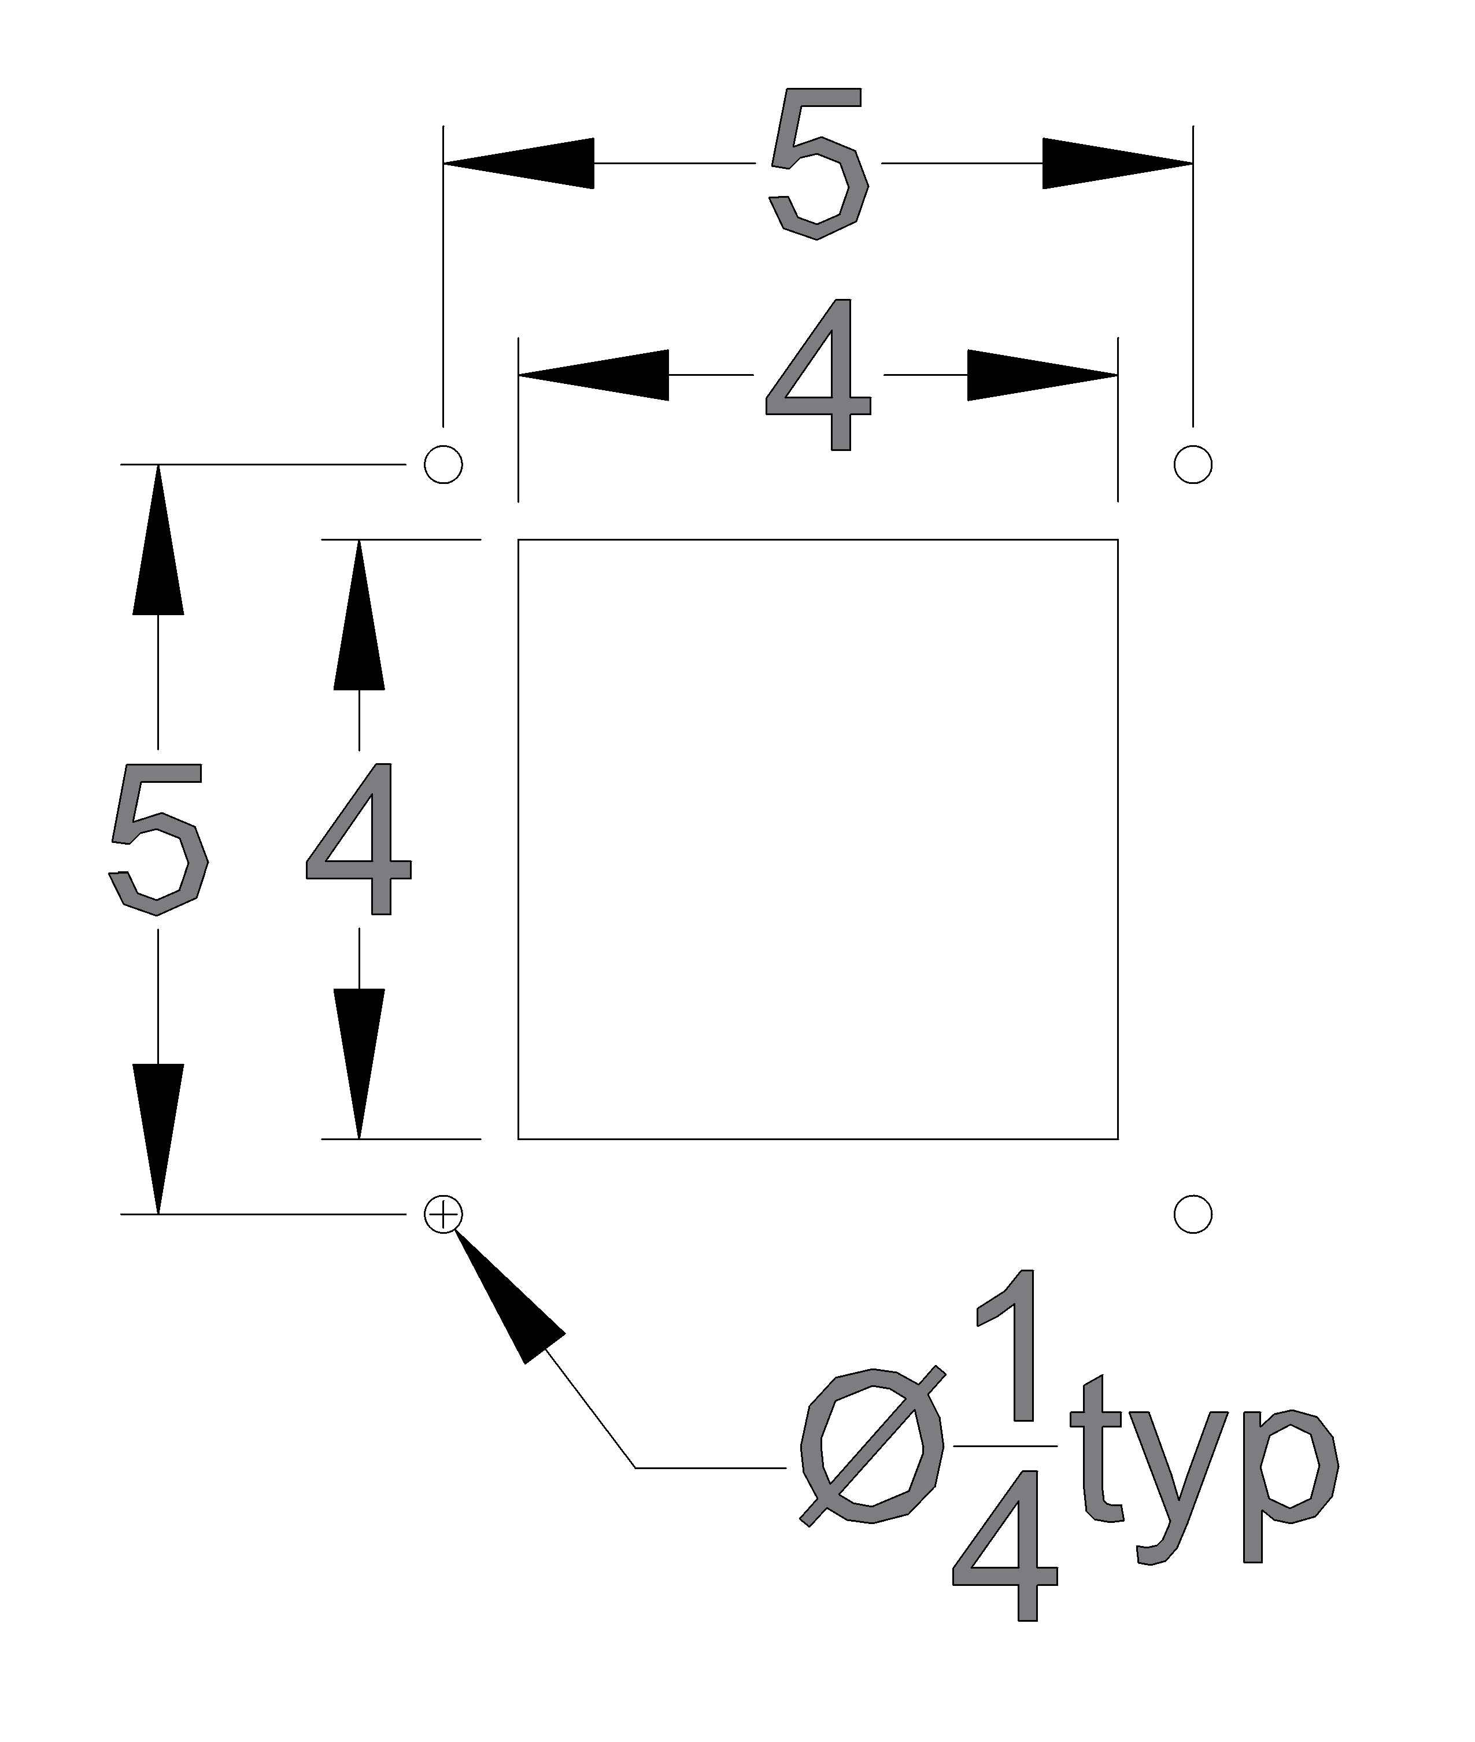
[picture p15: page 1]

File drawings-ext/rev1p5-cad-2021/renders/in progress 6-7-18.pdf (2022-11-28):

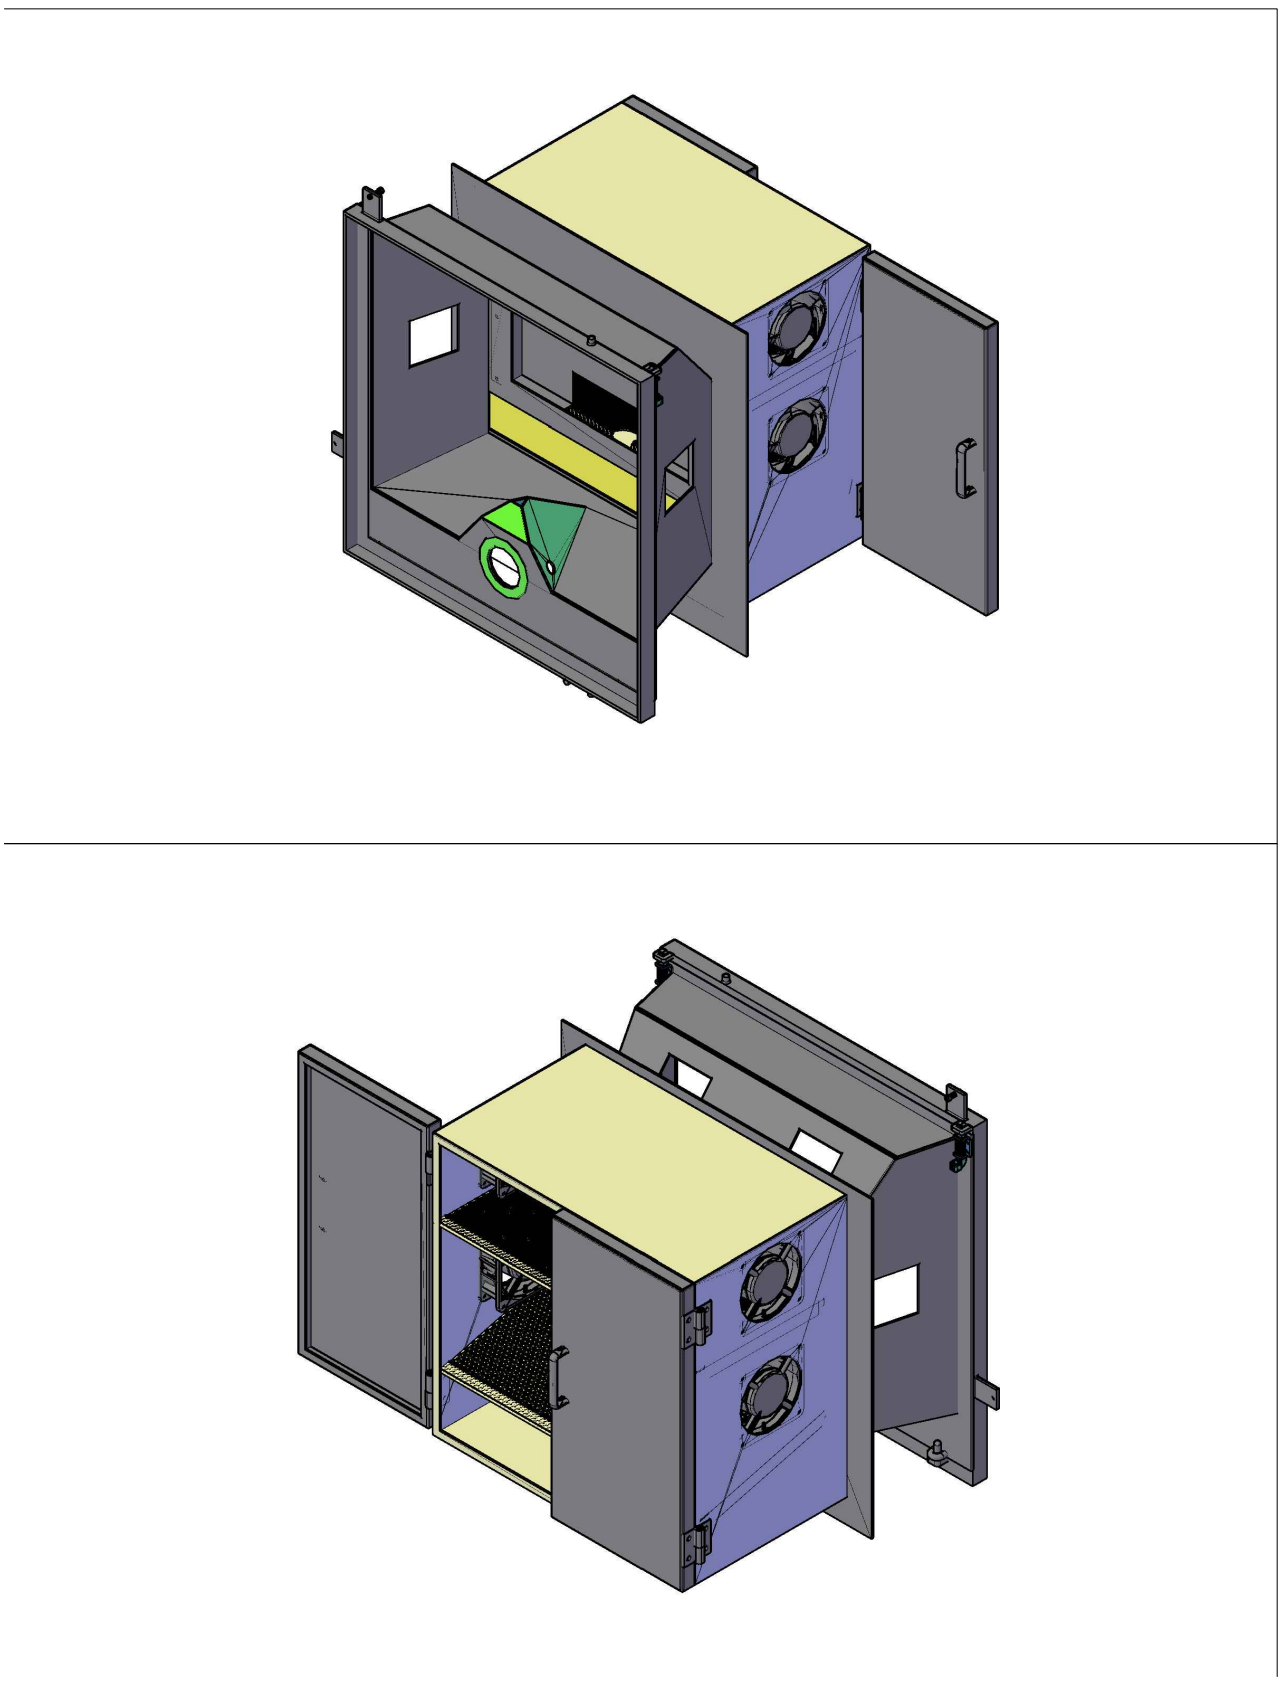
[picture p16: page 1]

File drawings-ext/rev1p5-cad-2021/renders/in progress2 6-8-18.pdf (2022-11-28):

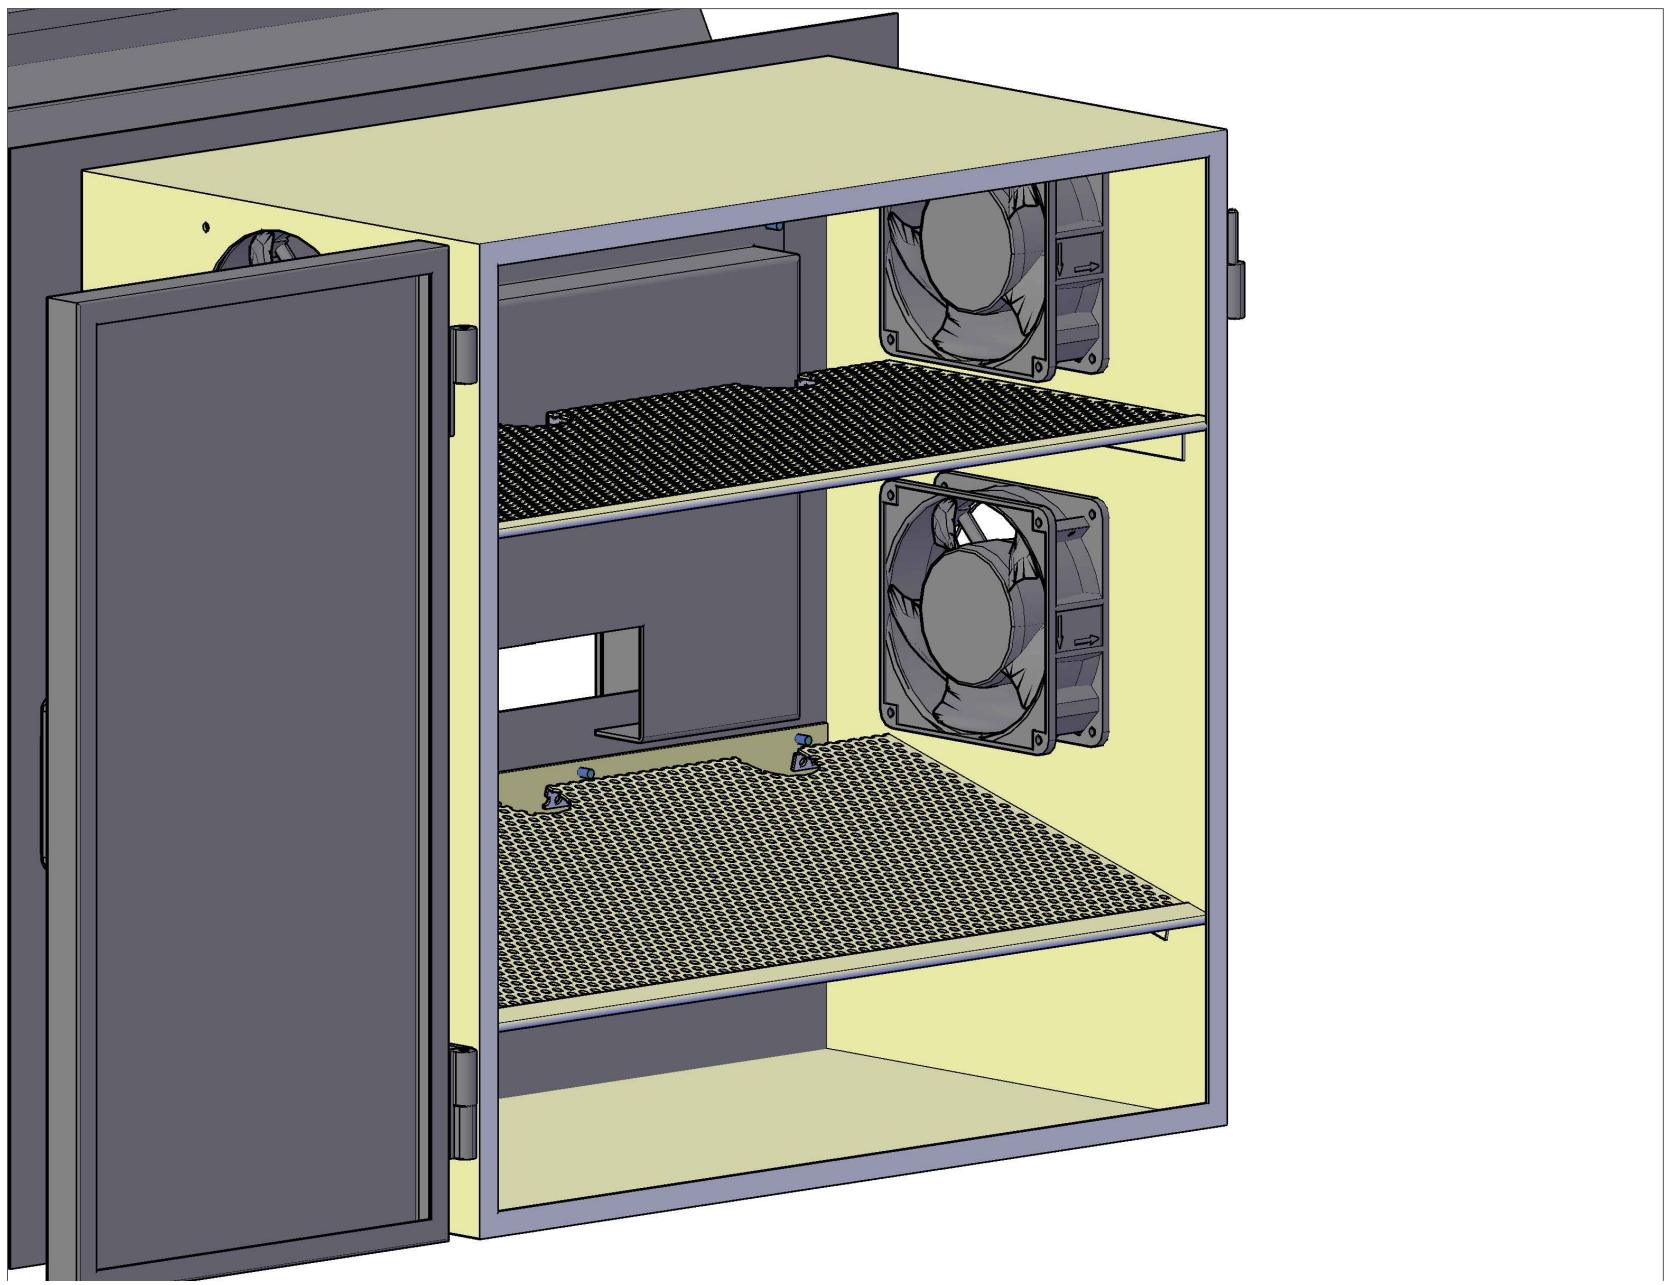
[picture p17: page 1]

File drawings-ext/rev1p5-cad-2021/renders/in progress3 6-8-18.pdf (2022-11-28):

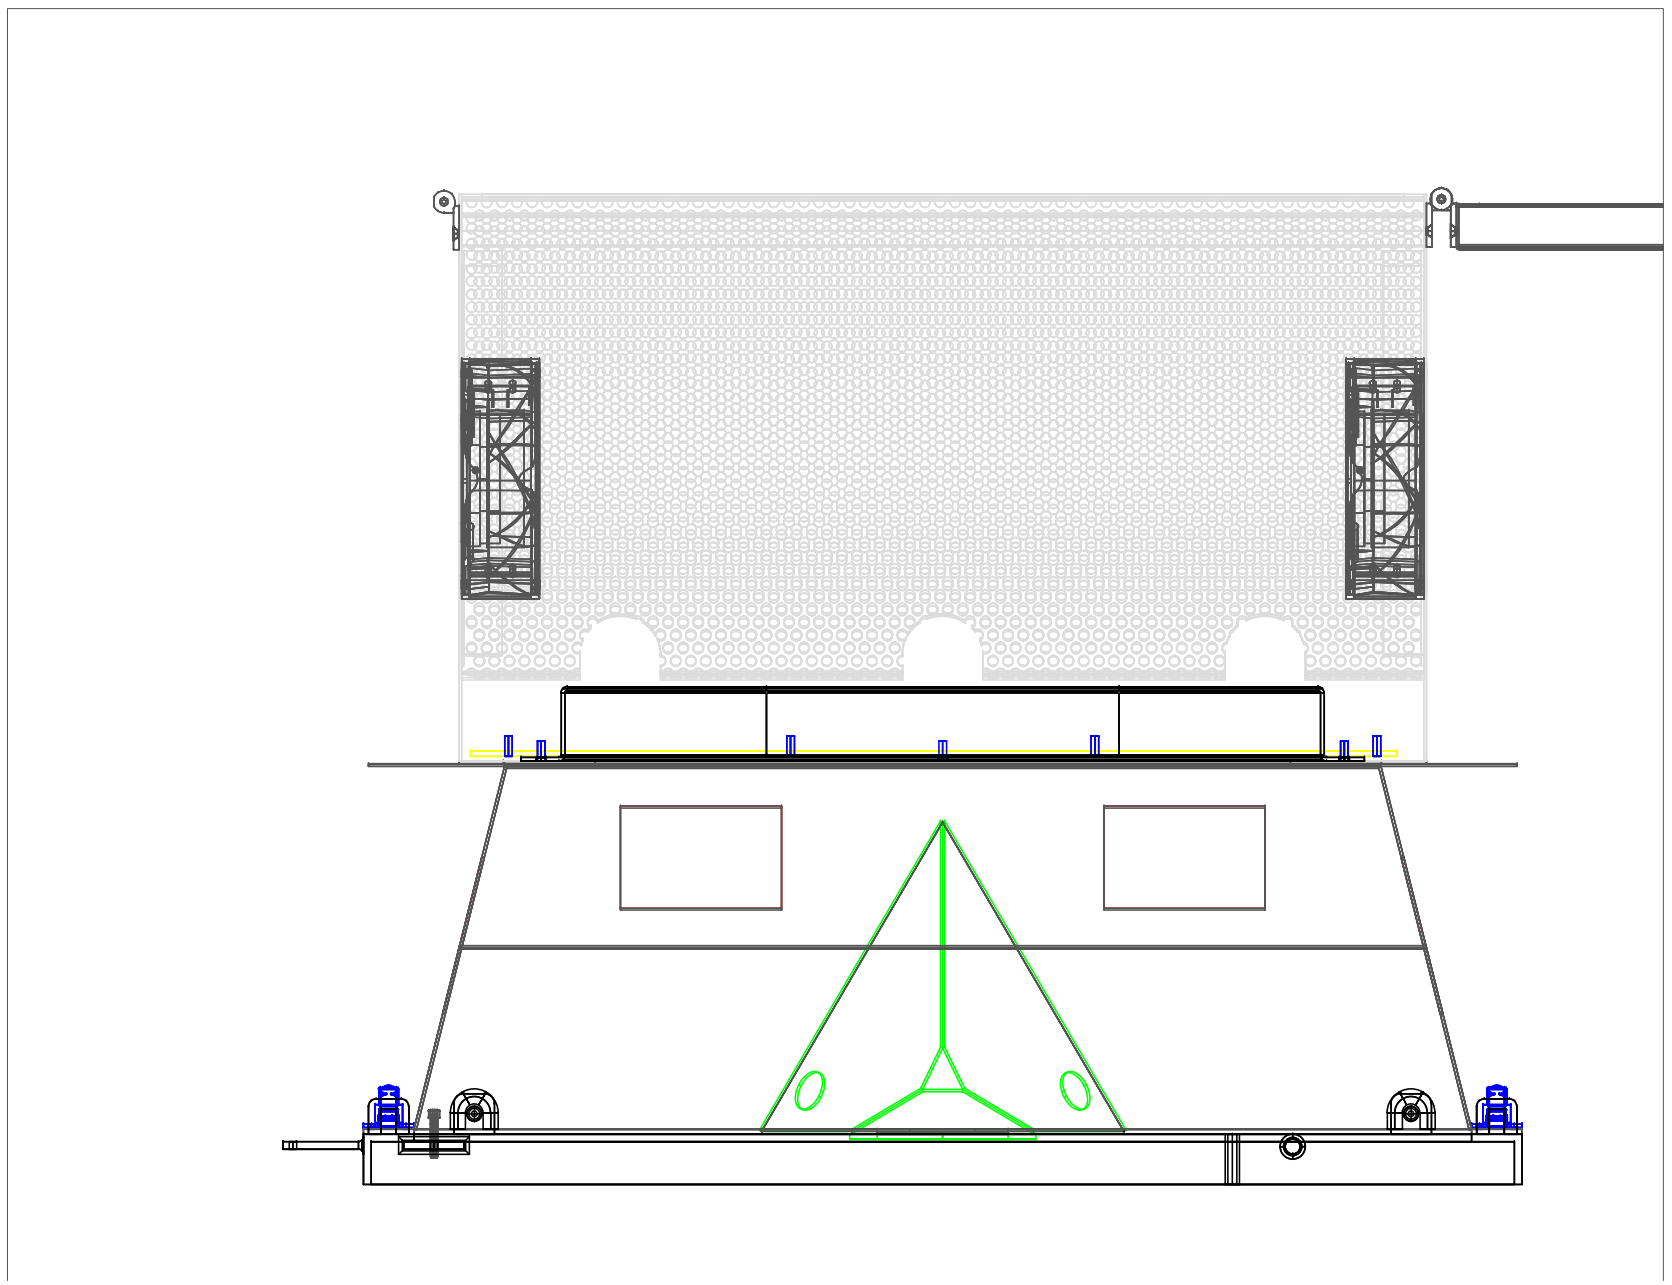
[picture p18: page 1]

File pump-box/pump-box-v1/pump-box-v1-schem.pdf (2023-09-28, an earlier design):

## To Pump

## To Arduino

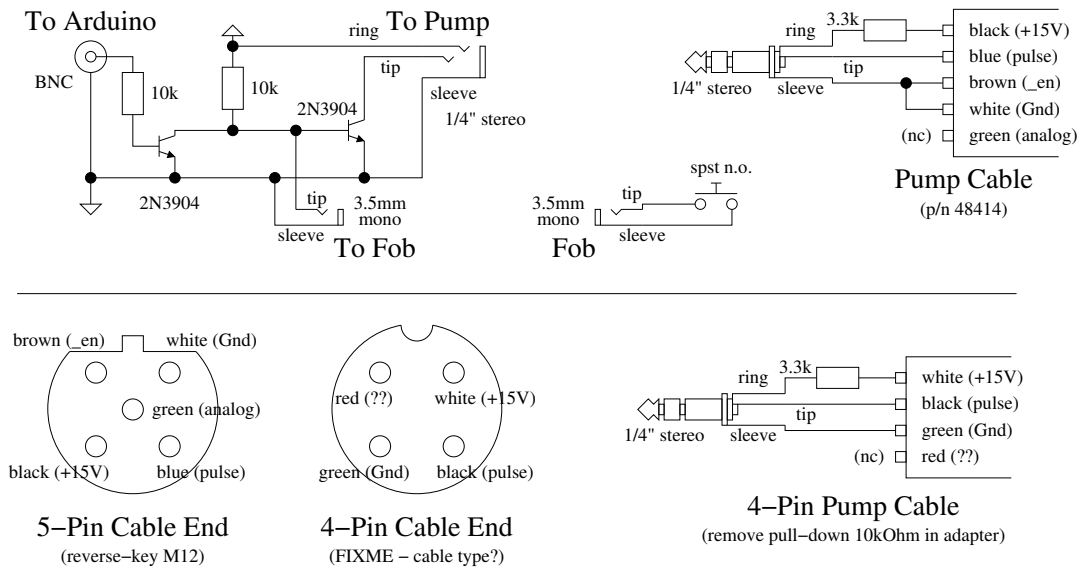
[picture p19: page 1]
BNC; tip; ring; sleeve; 1/4" stereo; 3.5mm mono; black (+15V); blue (pulse); brown (_en); white (Gnd); green (analog); Pump Cable; white (+15V); black (pulse); green (Gnd); red (??); (reverse−key M12); mono; spst n.o.; Fob

sleeve To Fob

4−Pin Pump Cable

5−Pin Cable End

4−Pin Cable End

(remove pull−down 10kOhm in adapter)

(FIXME − cable type?)

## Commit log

2021-02-10 Added miscellaneous notes.
    [kiosk-unity-machine-bom-202011.csv]
2021-02-10 Added proximity sensor evaluation.
2021-02-10 Added proximity sensor datasheets.
2021-02-10 Added pump box design information.
2021-02-10 Added reference information for parts, and vendor manuals for the pump.
2021-02-10 Moved wiring diagram to its own folder (from manual).
2021-02-10 Added README. Moved vendor materials out of 'reference'.
2021-02-15 Added power consumption notes and related vendor documents.
2022-11-28 Added a cleaned-up version of Adrian's development files for the Revision 2 kiosk station.
    [10_2 stainless 7 ga.dxf, 11_1 stainless 11 ga.dxf, 12_2 alum 1875.dxf, 13_2 alum 0625.dxf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]
2022-12-09 Renamed rev2 to rev1p5. Added Seattle cage adapter drawings.
    [10_2 stainless 7 ga.dxf, 11_1 stainless 11 ga.dxf, 12_2 alum 1875.dxf, 13_2 alum 0625.dxf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]
2022-12-09 Added best-guess CAD model of Vanderbilt kiosk adapter ring. Still needs drawings.
    [adapter-rev2-frame.iges, adapter-rev2-frame.step, adapter-rev2.fcstd]
2023-08-23 Added part numbers for old pump, new pump, and cable. Added new pump manual.
2023-09-28 Updated part number for 3.5mm audio jack.
2023-09-28 Added 4-pin cable wiring and pinouts for 4- and 5-pin cables to pump box schematic.
2023-10-16 Added all-in-one photo of pump cable plug assembly steps.
2023-11-03 Moved pump box to pump box v1.
2023-11-03 Added datasheets and BOM for v2 pump box.
2023-11-03 Started pump box v2 pcb.
2023-11-06 First draft of v2 pump box PCB.
    [pump-box-v2.bottom.gbr, pump-box-v2.bottommask.gbr, pump-box-v2.bottomsilk.gbr, pump-box-v2.fab.gbr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]
2023-11-06 Added cable gland to BOM and added datasheet.
2023-11-06 Started v2 enclosure design.
    [pumb-box-v2-pcb.iges, pump-box-v2-case.fcstd]
2023-11-08 Made mockup of bottom shell without ears.
    [pump-box-v2-case.fcstd]
2023-11-09 Finished adding ears to pump box shell. Lengthened by 0.25in for easier wiring.
    [pump-box-v2-case.fcstd]
2023-11-09 Made rounded versions of mockup case. Added meshes for mockup case.
    [case-mockup-bottom-ears.stl, case-mockup-bottom-plain.stl, case-mockup-plate.stl, case-mockup-top.stl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]
2023-11-09 Added meshes to v2 pump box release package. Updated release package.
2023-11-17 Added photos of v2 pump box.
2023-11-22 Clarified injection molding requirements. Added makefile support for cable adapter-plus-fob (two objects).
    [pump-box-v2.bottom.gbr, pump-box-v2.bottommask.gbr, pump-box-v2.bottomsilk.gbr, pump-box-v2.fab.gbr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]
2023-11-22 Added BOM for pump fob.
2023-11-22 Added pump fob PCB.
    [pump-fob-v2.bottom.gbr, pump-fob-v2.bottommask.gbr, pump-fob-v2.fab.gbr, pump-fob-v2.outline.gbr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]
2023-11-22 Added CAD for pump fob case.
    [audio-jack-cp-3523mjct-nd.iges, pcb-pump-box-v2.iges, pump-fob-case-v2.fcstd, screw-4-40-3f8.iges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]
2023-11-22 Exported meshes and IGES models for pump fob.
    [pump-fob-case-v2.fcstd, pump-fob-v2-shell-bottom.iges, pump-fob-v2-shell-bottom.stl, pump-fob-v2-shell-top.iges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]
2023-11-27 Added design-rule-check from vendor for pump fob injection molding. Handy for reference.
